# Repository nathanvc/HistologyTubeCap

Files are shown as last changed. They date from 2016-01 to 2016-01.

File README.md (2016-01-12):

# HistologyTubeCap
3D printable tube strainer cap for processing histological tissues.

Nathan Vierling-Claassen, Designed in consultation with Kevin Bath and Gabriela Manzano Nieves

12/2015, revised 1/2016

OpenSCAD design & STL file

--Tube strainer cap for processing histological tissue

--allows filling (open setting), straining (strainer setting) and stirring (close setting) without changing cap or tube

--Cap fits on Fischer Scientific 2mL MCT Graduated Tubes, 05-408-146

--Glue small square of nylon mesh over rectangular frame, and then fit into sliding cap

--Nylon stockings work, but stretch firmly before gluing

--Print quality should be quite high in order for slider to work smoothly 

--Printed with support from the build surface

--Remove support material carefully with scalpel or dental pick to ensure good fit over tube

--Test prints were with ABS on a Lulzbot Taz4 with hexagon print head upgrade (which is essentially a Taz5) at fine resolution (0.16 layer height)

--measurements are in mm (standard for openSCAD)

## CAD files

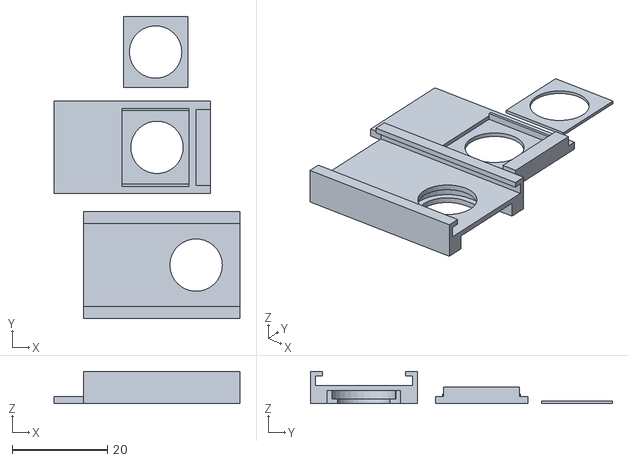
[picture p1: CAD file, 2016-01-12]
tubestrainer_v5_slide_frame.stl
39.0 x 63.3 x 6.75

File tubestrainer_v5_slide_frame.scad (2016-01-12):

//----------------------------
// tubestrainer_v5_slide_frame
//----------------------------
// Nathan Vierling-Claassen
// Designed in consultation with Kevin Bath and Gabriela Manzano Nieves
// 12/2015, revised 1/2016
// OpenSCAD design
//---------------------------
// --Tube strainer cap for processing histological tissue
// --allows filling (open setting), straining (strainer setting), 
// and stirring (close setting) without changing cap or tube.
// --Cap fits on Fischer Scientific 2mL MCT Graduated Tubes, 05-408-146
// --Glue small square of nylon mesh over rectangular frame, and then fit into sliding cap
// --Nylon stockings work, but stretch firmly before gluing
// --Print quality should be quite high in order for slider to work smoothly 
// --Printed with support from the build surface
// --Remove support material carefully with scalpel or dental pick
// to ensure good fit over tube
//--Test prints were with ABS on a Lulzbot Taz4 with hexagon print head
// upgrade (which is essentially a Taz5) at fine resolution (0.16 layer height)
//-- measurements are in mm (standard for openSCAD)
//---------------------------
$fn=30;

// tube top diam
diam_tp=13.4;

// tube base diam (diameter under ridge)
diam_b=11;

// depth of groove for sliding over top of tube
d_gv=1.75;

// thickness of walls throughout
th=1;

// thickness for the thin cap to cover nylon fabric
th_c=0.5;

// depth of groove for slider
gv_d=1;

// thickness of sliding cap
sl_th=1.5;

// clearance for sliding cap groove
// NOTE: this can be adjusted if slider is to tight/loose on your printer
sl_cl=0.5;

// extra width of slider to allow for gluing screen 
sl_gl=1.5;

// width of ridge around gluing area (protects sliding space 
// from glue/nylon interference)
gl_w=0.5;

// width of sliding cap (allows for extra width for gluing screen)
sl_w=diam_tp+2*sl_gl+2*sl_cl+2*gv_d;

// width of handle tab for slider
t_w=3; 

// height of handle tab for slider
t_h=2;  

// change print direction from original for the tube cap
// (an earlier design without sliding top printed the opposite direction in z)
rotate(180,[0, 1, 0]) {
    
//----------------------------------    
// Make topper that attaches to tube
// ---------------------------------    
    difference(){
        // outer body of tube cap
        translate([-0.5*diam_tp-th-sl_gl,-sl_w/2-th-sl_cl,-sl_th-sl_cl-th])
            cube([2*diam_tp+sl_gl+gv_d+sl_cl+t_w,sl_w+2*th+2*sl_cl,d_gv+2*th+sl_th+sl_cl+th]);
        union(){
            // remove inner cylinder
            cylinder(h=20, r=diam_b/2, center=true);
            // remove slightly larger cylinder to make opening that slides onto tube
            translate([0,0,th])cylinder(h=d_gv, r=diam_tp/2);
            // remove cubes at front that extend opening on tube topper groove
            translate([-diam_tp,-diam_tp/2,th])cube([diam_tp, diam_tp , d_gv]);
            // remove wider opening at front to make it easier to load tube
            translate([-diam_tp-4,-diam_tp/2-th,th])cube([diam_tp, diam_tp+2*th , d_gv+2*th]);
            // extend narrower lower portion of groove for tube to the front
            translate([-diam_b,-diam_b/2,th])cube([diam_b, diam_b , d_gv+2*th]);
            // remove inside wider portion of slider opening for top
            translate([-1.5*diam_tp-sl_gl,-sl_w/2-sl_cl,-sl_th-sl_cl])
                cube([4*diam_tp+2*sl_gl,sl_w+2*sl_cl,sl_th+sl_cl]);
            // remove more narrow opening on top of slider groove
            translate([-1.5*diam_tp+gv_d-sl_gl,-sl_w/2+gv_d,-sl_th-sl_cl-th])
                cube([4*diam_tp+2*sl_gl,sl_w-gv_d*2,sl_th+sl_cl+th]);
        }
    }

// ---------------------------
// Make sliding top (2 pieces)
// ---------------------------
      // Main Portion of Sliding top
      //----------------------------
      // shift this downward, so that bottom of both parts are at same location in z-axis
      // shift in y so parts not joined      
      translate([0,15,d_gv+2*th-sl_th]){
        difference(){
            union(){
                // body of sliding top
                translate([-t_w,0,0])cube([2*diam_tp+sl_gl+gv_d+sl_cl+t_w, sl_w, sl_th]);
                // handle for moving sliding top
                translate([-t_w,1.5*sl_cl+gv_d,-t_h])cube([t_w,sl_w-t_w*sl_cl-2*gv_d,t_h]);
                // thin ridges at edge of opening to protect slider from glue/nylon
                translate([gv_d+sl_cl, +gv_d+sl_cl, -gl_w])
                difference(){
                    cube([diam_b+2*sl_gl, sl_w-2*gv_d-2*sl_cl,gl_w]);
                    translate([0,gl_w,0])
                    cube([diam_b+2*sl_gl, sl_w-2*gv_d-2*sl_cl-2*gl_w,gl_w]);
                }
            }
            union(){
                // remove cylindrical opening for nylon strainer
                translate([diam_tp/2+sl_gl, sl_w/2,0]) cylinder(h=5, r=diam_b/2);
                // remove opening for frame for nylon to fit above screened opening
                translate([gv_d+sl_cl, gv_d+sl_cl+gl_w, -gl_w+sl_th/2-0.25])
                    cube([diam_b+2*sl_gl, sl_w-2*gv_d-2*sl_cl-2*gl_w, sl_th/2]); 
            }          
        }
        // separate thin frame to glue nylon to, 
        // fits into slider after nylon is glued, some fiddling to get clearance between pieces 
        //---------------------------------
        // shift to own print error and such that print surface is same as other parts
        translate([gv_d+sl_cl, gv_d+sl_cl+gl_w+20, d_gv+2*th-2*sl_th+0.2]) 
                difference(){
                    translate([0.25,0.25,0])cube([diam_b+2*sl_gl-.5, sl_w-2*gv_d-2*sl_cl-2*gl_w-.5, sl_th/2-0.2]); 
                    translate([diam_b/2+sl_gl,(sl_w-2*gv_d-2*sl_cl-2*gl_w)/2,0]) cylinder(h=5, r=diam_b/2);
                }
        }
}
